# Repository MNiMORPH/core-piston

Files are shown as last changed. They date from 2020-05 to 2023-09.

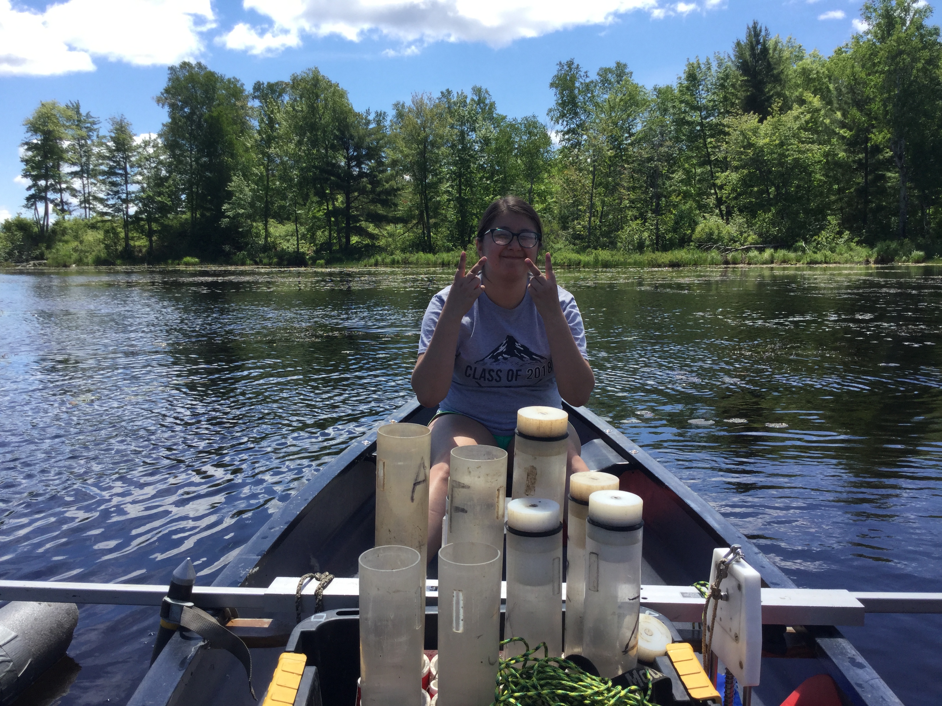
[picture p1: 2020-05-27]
images/IMG_4434.JPG

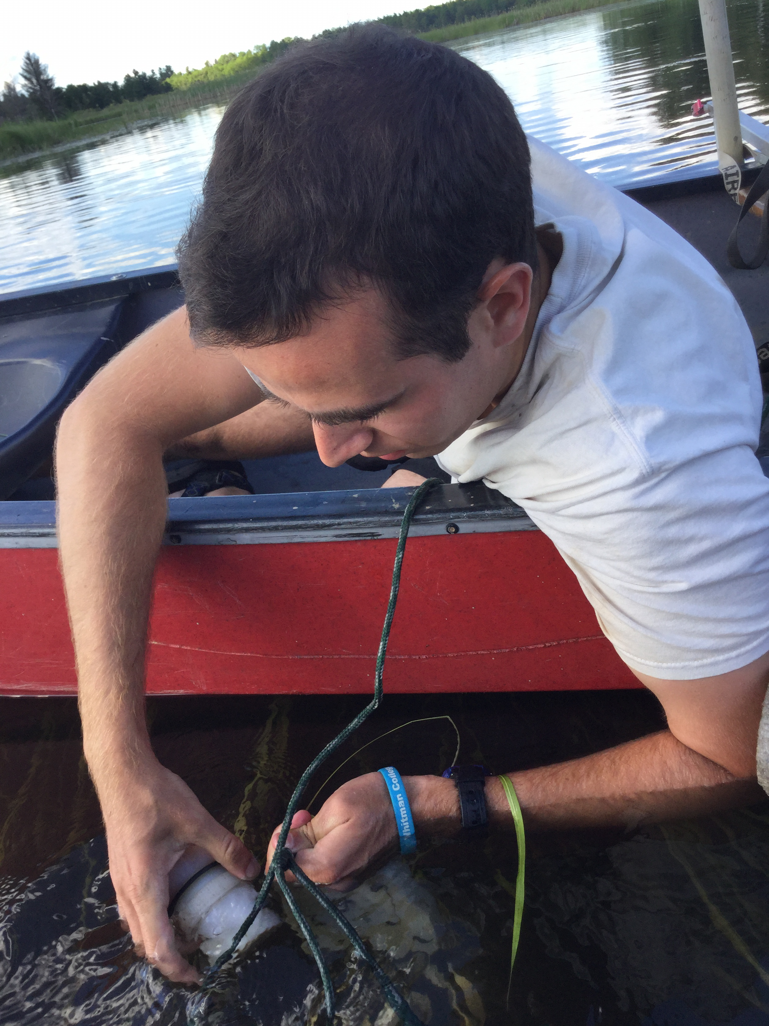
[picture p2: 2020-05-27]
images/IMG_4460.JPG

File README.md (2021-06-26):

# core-piston

***3D-printable piston to hold a sediment core in its barrel***

**Design by [Bobby Schulz](https://github.com/bschulz1701); documentation by [Andy Wickert](https://github.com/awickert); testing and additional documentation by [Alex Waheed](https://github.com/alexwaheed).** Please attribute following CC BY-SA 4.0 (see the [license](LICENSE))

***[Add persistent Zenodo link and DOI here once these are generated.]***

This core piston is made to work with a Pylonex HTH Gravity Corer with a 70mm tube diamter. The honeycomb structure within the 3D print ensures that it floats when invariably dropped into the water.

## Materials

* Plastic body
  * Two 3D-printable components
  * **SUGGESTED FILL DENSITY? Get from PRUSA Slic3r with SD card gcode**
  * Suggested material: White or brightly colored ABS
* Rubber seal
  * Rubber sheet: [1/8" thick, durometer 60A](https://www.mcmaster.com/8716K24-8716K162/). Get a bigger one than this 6"x6" sheet if you want to make more, of course!
  * Circular cutter and hole punch, unless you have a laser cutter. **@awickert: give McMaster items once proving that they actually work.** **@bschulz1701: Diameter**
* Fasteners
  * Screws: [1-1/2" long 1/4"-20 flat head hex drive](https://www.mcmaster.com/92210A546/). You probably don't need the hex drive part ;) but the rest is important, as is the angle made by the bottom flat head (because our countersunk hole fits it).
  * Threaded inserts: [1/4"-20 Pull-out-resistant](https://www.mcmaster.com/90363A034/).

## Instructions

Here, "bottom" refers to the plastic part that is held by the user, and "top" refers to the plastic part that is in direct contact with the core. These are connected by screws once assembly is complete.

1. Generate gCode for your 3D printer. We use [Slic3r with a Prusa 3D printer](https://www.prusa3d.com/prusaslicer/).
2. Print using ABS. We suggest a bright color that you can see amidst the muck.
3. Cut rubber rounds **diameter**. We use a laser cutter, but a compass with a pen knife should work well too. **@awickert: Add McMaster tools once verified**
4. Cut holes for the three screws (1/4") using the laser cutter or a punch **@awickert: Same as above**
5. Install threaded inserts into the bottom printed component. **@bschulz1701: installation method depends on type -- any info here?**
6. Place the top component atop the gasket and bottom component, sandwiching the gasket betweent the two plastic parts.
7. Insert the three screws, piercing the rubber gasket in the process. **@bschulz1701 or do you cut holes in the gasket beforehand?** Ensure that these are tight
8. Inspect your piston for any obvious problems, and test it in the lab with a core barrel.

## Rendered images

Images from bottom to top in the direction from user's hand inserting the piston to top of core barrel.

### Bottom

This bottom portion of the piston is counterintuitively called ["Plug Top"](https://github.com/umn-earth-surface/core-piston/blob/master/Plug_Top_MultiHole.STL). Maybe we'll change the name.

Bottom

***Bottom plastic component of core piston.*** *The thinner portion to the lower right is held to insert the piston into the core barrel in order to seal it and keep the core from falling out. Not visible is a hole that goes partway through the piston and can be used with a dowel to extrude the core out of the top of the barrel. On the upper left are three holes to hold threaded inserts for screws that connect the top half and bottom halves of the piston. A circular rubber gasket sits between these two halves, held in place by the screws.*

Bottom of top

***Bottom side of top plastic component of core piston.*** *Screws pass between the three holes shown here, through the rubber gasket, and into the bottom plastic component (shown above). The angled edges of this component force the rubber gasket to bend towards the bottom of the piston, pinning it to the mating angled faces on the bottom plastic component. This ensures that the piston may extrude the core, but locks it against sliding downwards.*

### Top

This top portion of the piston is counterintuitively called ["Plug Base"](https://github.com/umn-earth-surface/core-piston/blob/master/Plug_Base_MultiHole.STL). Again, maybe we'll change the name. Or maybe not.

Top of top

***Top side of top plastic component of core piston.*** *This side of the piston directly contacts the bottom of the core. The three countersunk holes hold the screws and ensure that their heads are flush with the remainder of the surface.*

<br>
<br />This work is licensed under a <a rel="license" href="http://creativecommons.org/licenses/by-sa/4.0/">Creative Commons Attribution-ShareAlike 4.0 International License</a>.

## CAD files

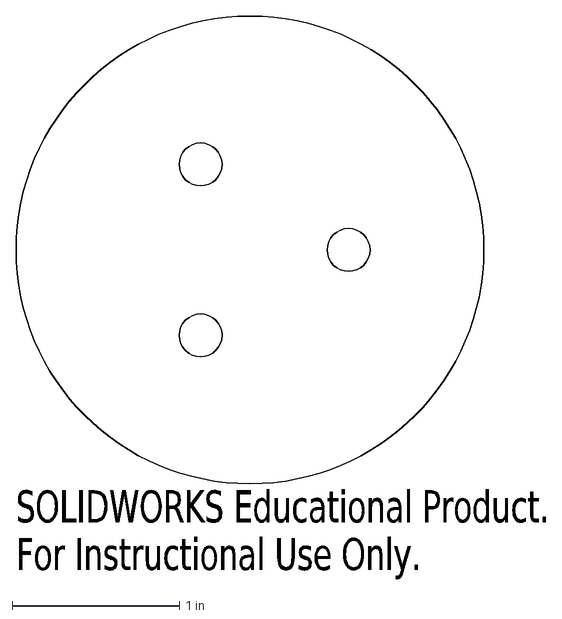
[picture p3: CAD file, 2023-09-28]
Gastket_MultiHole.DXF
SOLIDWORKS Educational Product.
For Instructional Use Only.

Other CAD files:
Plug_Base_MultiHole.SLDPRT
Plug_Top_MultiHole.SLDPRT
Plug_Base_MultiHole.STL
Plug_Top_MultiHole.STL

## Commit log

2020-05-25 CAD models to LFS
    [Plug_Base_MultiHole.SLDPRT, Plug_Base_MultiHole.STL, Plug_Top_MultiHole.SLDPRT, Plug_Top_MultiHole.STL]
2021-06-23 No heat concerns on print
2021-06-23 Rubber rounds and hole punching
2021-06-23 Tech Specs --> actually, materials
2021-06-26 Threaded inserts: pull-out resistant
2023-09-28 Added DXF file for gasket
    [Gastket_MultiHole.DXF]
